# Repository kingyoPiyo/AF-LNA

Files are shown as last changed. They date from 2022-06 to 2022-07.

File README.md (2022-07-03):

# AF-LNA
ADA4522-2ARMZ を 4パラで使用した低周波用のローノイズアンプです。  
帯域は 0.1～1000Hz、ゲインは 60dB、ノイズは 5nV/√Hz 以下となるように設計しています。  
⇒ 実測で 3.2nV/√Hz 程度となりました

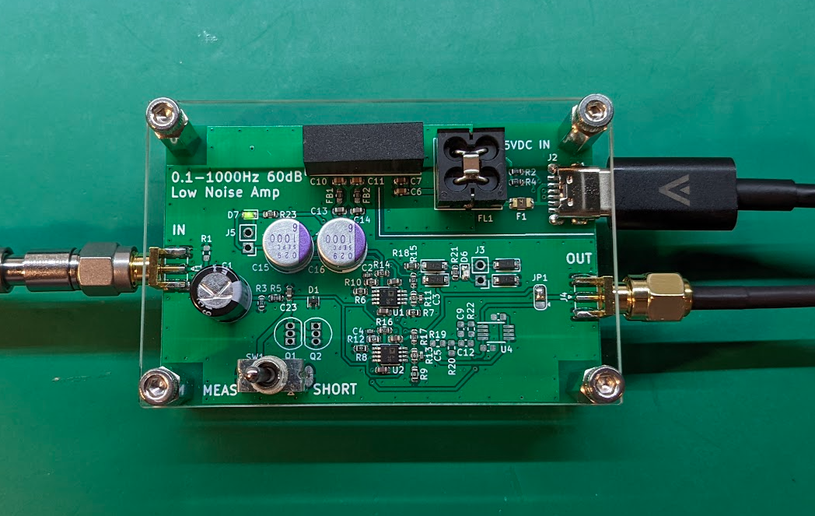
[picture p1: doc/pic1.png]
  
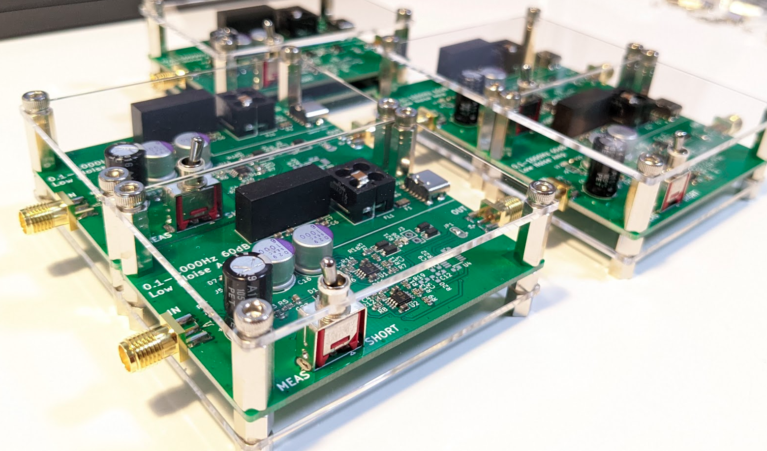
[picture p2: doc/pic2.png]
  

## 主な仕様
| 項目 | 仕様 |
| ---- | ---- |
| 電源電圧 | 5V±0.5V（USB-C端子より供給） |
| 消費電流 | 50mA 以下 |
| 電圧利得 | 60dB（1000倍） |
| 電圧利得周波数特性 | 0.1～1000Hz（-3dB） |
| 入力換算雑音電圧密度 | 3.2nV/√Hz（typ） at 100Hz |
| 入力電圧範囲 | 入力保護クランプ ±0.5Vpp、DC 重畳は +30V 以下 |
| 入力結合 | AC結合（220uF、有極性コンデンサによる） |
| 入力インピーダンス | 10kΩ at 10～1000Hz |
| 出力インピーダンス | 120Ω at 10～1000Hz |
| 電源構成 | USB-C 側と回路の GND を絶縁型 DCDC により絶縁<br>（絶縁抵抗 100MΩ 以上 at DC500V） |
| 表示LED | 通電表示（D7：緑色）、出力クリッピング表示（D6：赤色） |

## PCB Image  
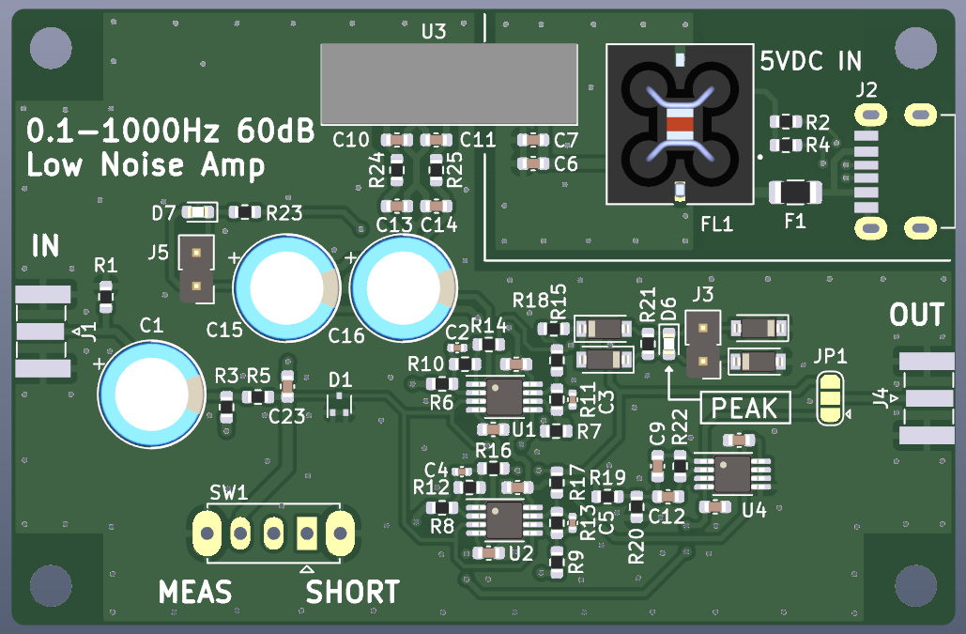
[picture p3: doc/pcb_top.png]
  
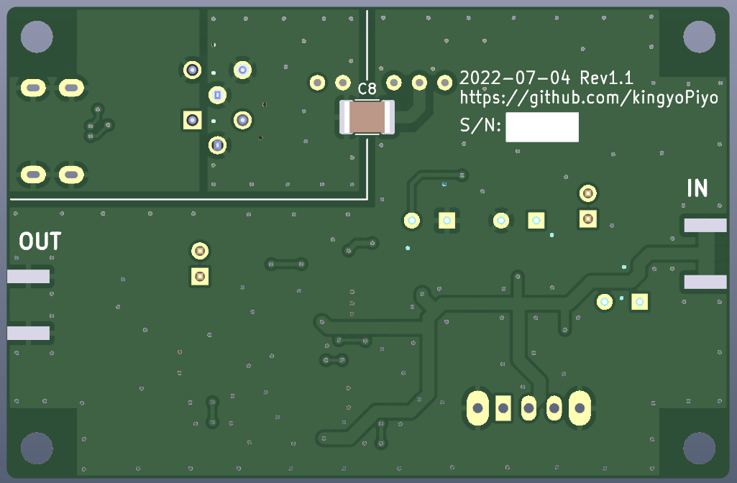
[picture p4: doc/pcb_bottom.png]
  

## Schematic
[Schematic.pdf](doc/schematic.pdf "Schematic")

## 開発環境
- KiCad Version 6.0.5

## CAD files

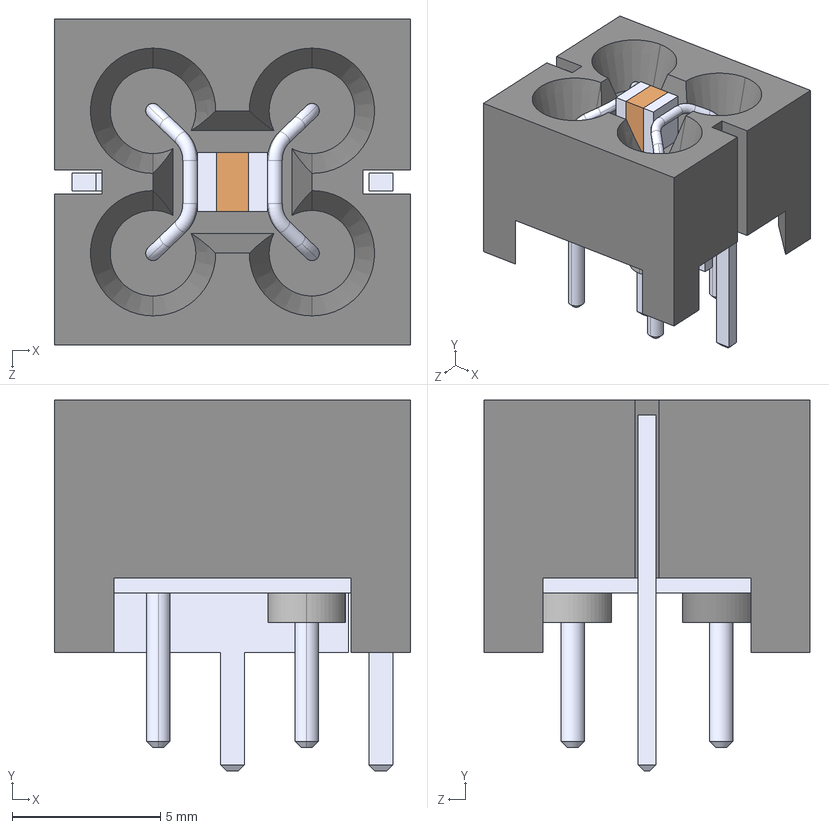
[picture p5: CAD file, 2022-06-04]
kicad/AF-LNA/3D/BNX016-01.step
12.0 x 12.5 x 11.0 mm

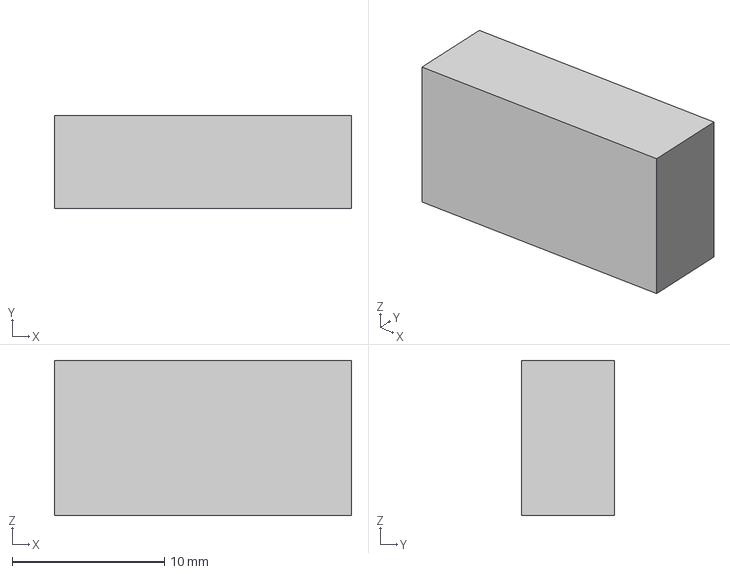
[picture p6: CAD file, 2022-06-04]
kicad/AF-LNA/3D/MAU106 v1.step
19.5 x 6.10 x 10.2 mm

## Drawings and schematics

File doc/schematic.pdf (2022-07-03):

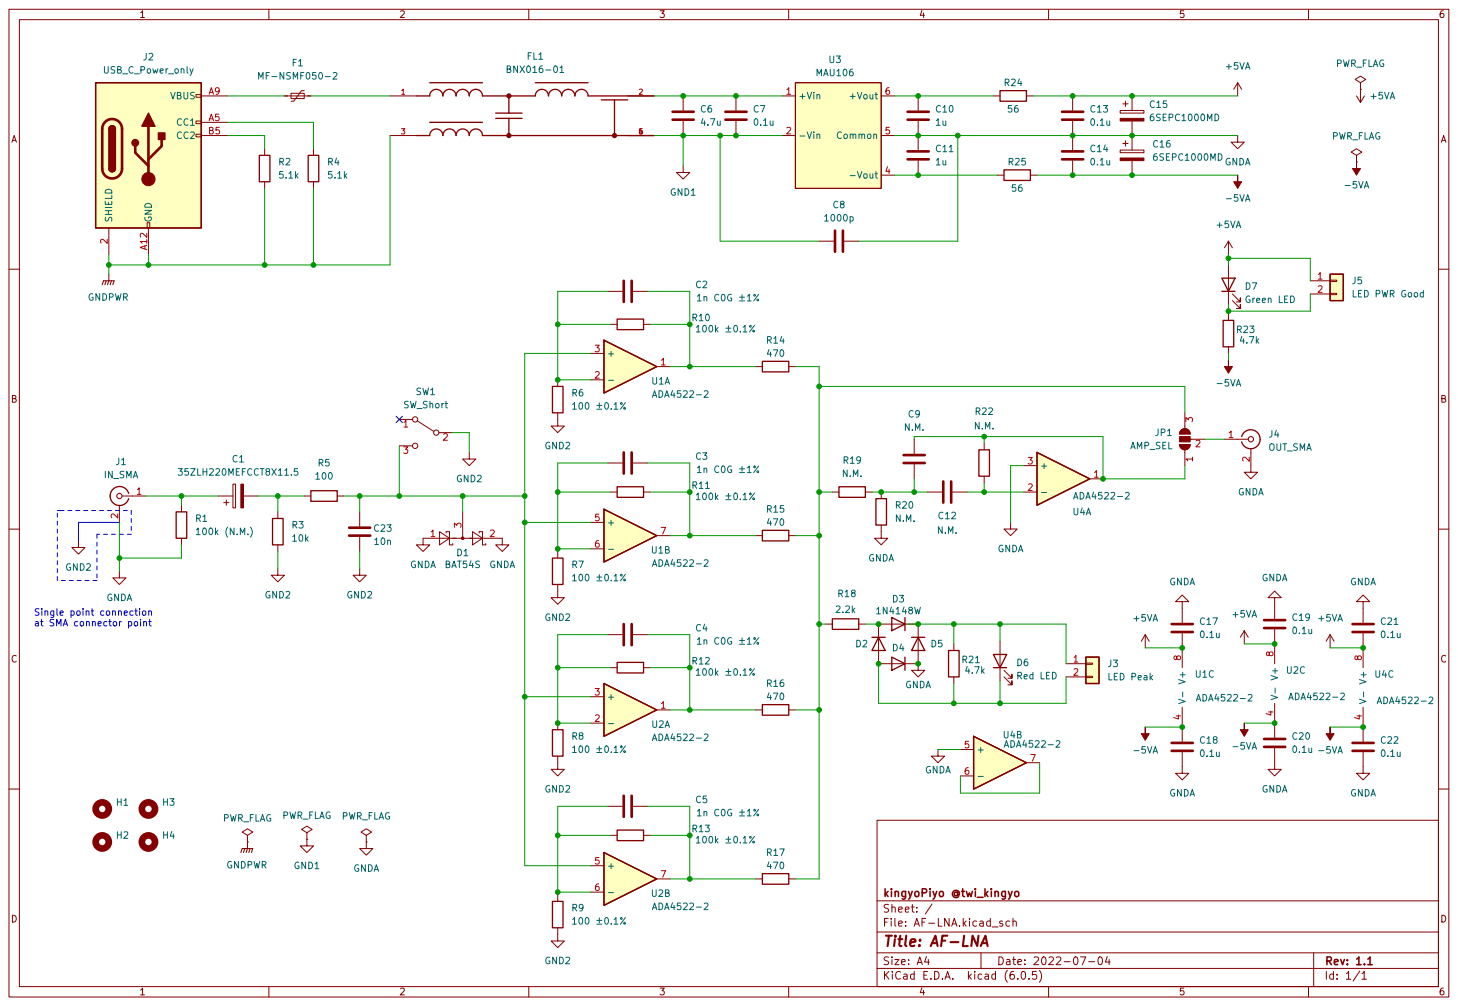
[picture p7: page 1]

at SMA connector point

File: AF-LNA.kicad_sch Sheet: / kingyoPiyo @twi_kingyo

Id: 1/1 Title: AF-LNA

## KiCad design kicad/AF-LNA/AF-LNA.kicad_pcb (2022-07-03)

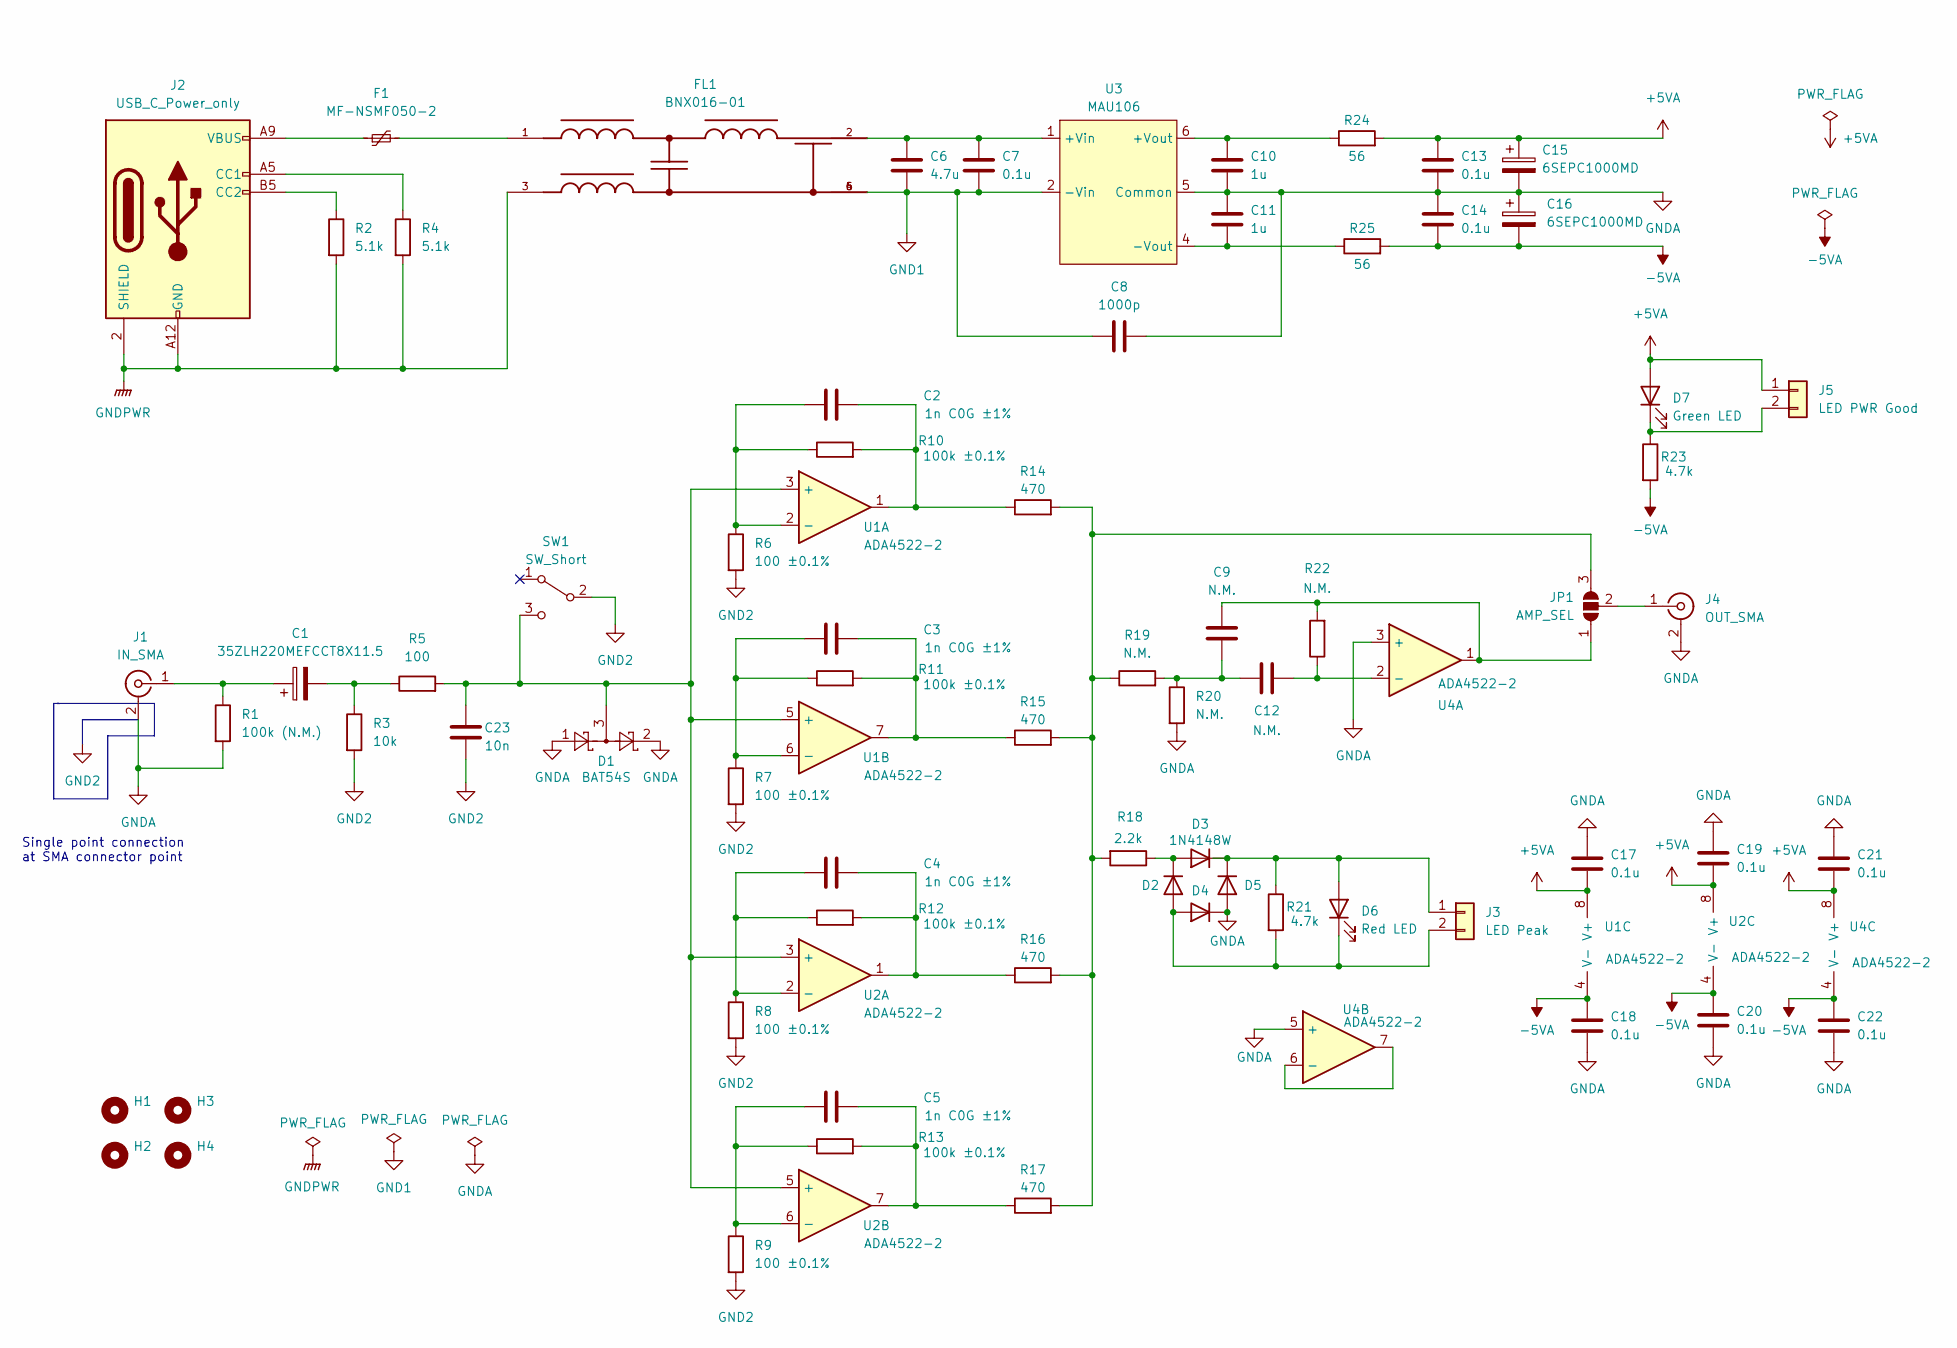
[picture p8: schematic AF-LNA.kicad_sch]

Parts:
C1: 35ZLH220MEFCCT8X11.5; CP_Radial_D8.0mm_P3.50mm
C2, C3, C4, C5: 1n C0G ±1%; C_0402_1005Metric
C6: 4.7u; C_0603_1608Metric
C7, C13, C14, C17, C18, C19, C20, C21, C22: 0.1u; C_0603_1608Metric
C8: 1000p; C_1812_4532Metric
C9, C12: N.M.; C_0603_1608Metric
C10, C11: 1u; C_0603_1608Metric
C15, C16: 6SEPC1000MD; CP_Radial_D8.0mm_P3.50mm
C23: 10n; C_0603_1608Metric
D1: BAT54S; SOT-523
D2, D3, D4, D5: 1N4148W; D_SOD-123
D6: Red LED; LED_0603_1608Metric
D7: Green LED; LED_0603_1608Metric
F1: MF-NSMF050-2; Fuse_1206_3216Metric
FL1: BNX016-01; FIL_BNX016-01
H1, H2, H3, H4: MountingHole; MountingHole_3.2mm_M3
J1: IN_SMA; S-063-49-TGG
J2: USB_C_Power_only; USB-C_Power_only
J3: LED Peak; PinHeader_1x02_P2.54mm_Vertical
J4: OUT_SMA; S-063-49-TGG
J5: LED PWR Good; PinHeader_1x02_P2.54mm_Vertical
JP1: AMP_SEL; SolderJumper-3_P1.3mm_Open_RoundedPad1.0x1.5mm
R1: 100k (N.M.); R_0603_1608Metric
R2, R4: 5.1k; R_0603_1608Metric
R3: 10k; R_0603_1608Metric
R5: 100; R_0603_1608Metric
R6, R7, R8, R9: 100 ±0.1%; R_0603_1608Metric
R10, R11, R12, R13: 100k ±0.1%; R_0603_1608Metric
R14, R15, R16, R17: 470; R_0603_1608Metric
R18: 2.2k; R_0603_1608Metric
R19, R20, R22: N.M.; R_0603_1608Metric
R21, R23: 4.7k; R_0603_1608Metric
R24, R25: 56; R_0603_1608Metric
SW1: SW_Short; 2MS1-T1-B4-VS2-Q-E-S
U1, U2, U4: ADA4522-2; MSOP-8_3x3mm_P0.65mm
U3: MAU106

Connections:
+5VA: C13.1, C15.1, C17.2, C19.2, C21.2, D7.2 (A), J5.1, R24.2, U1.8 (V+), U2.8 (V+), U4.8 (V+)
-5VA: C14.2, C16.2, C18.1, C20.1, C22.1, R23.2, R25.2, U1.4 (V-), U2.4 (V-), U4.4 (V-)
GND1: C6.2, C7.2, C8.1, FL1.4, FL1.5, FL1.6, U3.2 (-Vin)
GND2: C23.1, R3.2, R6.2, R7.2, R8.2, R9.2, SW1.2 (B)
GNDA: C8.2, C10.2, C11.1, C13.2, C14.1, C15.2, C16.1, C17.1, C18.2, C19.1, C20.2, C21.1, C22.2, D1.1, D1.2, D4.1 (K), D5.2 (A), J1.2 (Ext), J4.2 (Ext), R1.2, R20.2, U3.5 (Common), U4.3 (+), U4.5 (+)
GNDPWR: FL1.3, J2.2 (SHIELD), J2.A12 (GND), J2.B12 (GND), R2.2, R4.2
unnamed: C1.1, J1.1 (In), R1.1
unnamed: C1.2, R3.1, R5.1
unnamed: C2.1, R6.1, R10.1, U1.2 (-)
unnamed: C2.2, R10.2, R14.1, U1.1
unnamed: C3.1, R7.1, R11.1, U1.6 (-)
unnamed: C3.2, R11.2, R15.1, U1.7
unnamed: C4.1, R8.1, R12.1, U2.2 (-)
unnamed: C4.2, R12.2, R16.1, U2.1
unnamed: C5.1, R9.1, R13.1, U2.6 (-)
unnamed: C5.2, R13.2, R17.1, U2.7
unnamed: C6.1, C7.1, FL1.2, U3.1 (+Vin)
unnamed: C9.1, JP1.1 (A), R22.2, U4.1
unnamed: C10.1, R24.1, U3.6 (+Vout)
unnamed: C11.2, R25.1, U3.4 (-Vout)
unnamed: C9.2, C12.1, R19.2, R20.1
unnamed: C12.2, R22.1, U4.2 (-)
unnamed: D2.1 (K), D3.2 (A), R18.1
unnamed: D2.2 (A), D4.2 (A), D6.1 (K), J3.2, R21.2
unnamed: D3.1 (K), D5.1 (K), D6.2 (A), J3.1, R21.1
unnamed: F1.1, J2.A9 (VBUS), J2.B9 (VBUS)
unnamed: F1.2, FL1.1
unnamed: J2.A5 (CC1), R4.1
unnamed: J2.B5 (CC2), R2.1
unnamed: J4.1 (In), JP1.2 (C)
unnamed: D7.1 (K), J5.2, R23.1
unnamed: JP1.3 (B), R14.2, R15.2, R16.2, R17.2, R18.2, R19.1
unnamed: C23.2, D1.3, R5.2, SW1.3 (C), U1.3 (+), U1.5 (+), U2.3 (+), U2.5 (+)
unnamed: U4.6 (-), U4.7

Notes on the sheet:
Single point connection at SMA connector point

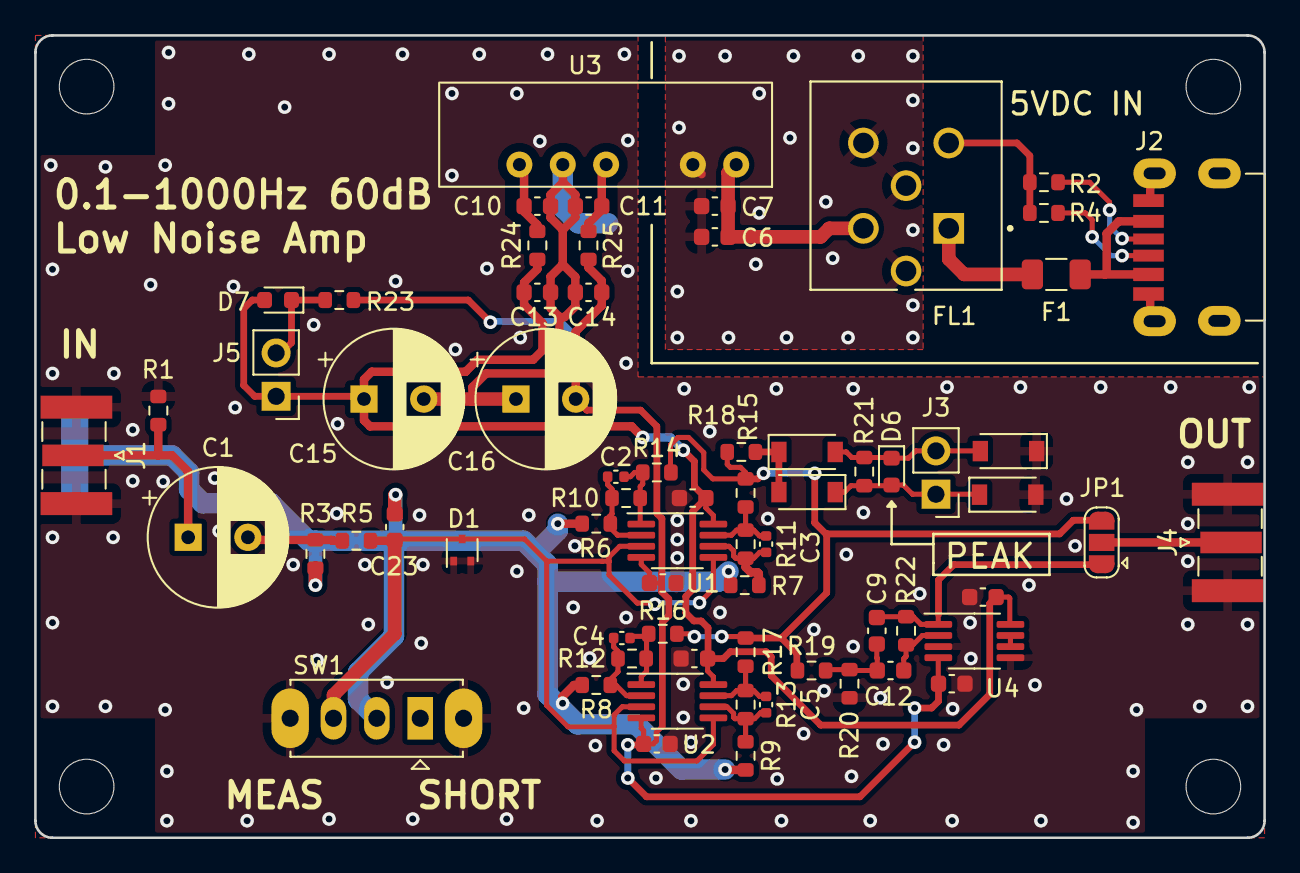
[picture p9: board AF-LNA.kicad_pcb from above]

Board: 2 copper layers, 72.0 x 47.0 mm, 72 parts (1 on the bottom side), 34 nets.

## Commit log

2022-06-04 Add some files
    [AF-LNA.kicad_pcb, AF-LNA.kicad_sch, BNX016-01.step, MAU106 v1.step]
2022-07-03 Update Rev1.1
    SW1位置変更、帰還抵抗GND配線をIN側SMA端子から取るように変更
    [AF-LNA.kicad_pcb, AF-LNA.kicad_sch]
